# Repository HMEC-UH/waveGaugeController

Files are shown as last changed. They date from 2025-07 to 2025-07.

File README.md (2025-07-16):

# Introduction/General Project Overview

This project was created in conjunction with Dr. Troy Heitmann's Wave Energy Research lab. In their lab, they use "Wave Gauges" to take the required measurements for their work. However, the calibration and movement of these gauges is an important part of the setup and usage: often this process is manual, imprecise, and frustrating for Dr. Heitmann and his fellow researchers. The purpose of this project was to create an automated process for the calibration and movement of these "Wave Gauges." 

## Project Breakdown

This project can be broken down into the following segments:

1. Physical design of calibration setup
2. Fabrication of calibration setup
3. Design of electrical systems
4. Fabrication of electrical systems
5. TCP Socket Connection (Information Transfer)
6. Clear User Interface (GUI)

## Physical Design of Calibration Setup

The design for the physical movement of the wave gauge is relatively minimalistic and simple. Using an internally outputting cycloidal gearbox to actuate a T12x3mm pitch lead screw and a close loop Nema 23 (along with the CL57T-V4.1 stepper driver), this system has +-0.5mm of control over the vertical actuation of the gauge (which is attached via screw clamping mechanism). There is a parallel "backbone" in the form of 8020 1010 extrusion. The carrier and lower reciever for the lead screw use offset 8020 1010 extrusion profiles (0.15mm) to achieve proper tolerance when mounting, and use t-nuts to properly clamp and attach onto the 8020 back rail. 

## Design of Electrical Systems

Again, the design of the electrical systems for this project is relatively simple. Using an Arduino Uno WiFi REV2 wired to a CL57T-V4.1 stepper driver (all powered by a 24V variable power supply), this system is able to be controlled over local WiFi.

## Programming

The code for this project was aimed to allow for a python-based GUI (with active feedback) that could send desired movement over local WiFi. It was a challenge using the WiFiNINA Arduino library to properly parse incoming requests from the Python GUI, but using the available "requests" library and PyQt5 (for GUI design), developing these two components was not extremely complex.

# Using Posted Resources

## Posted Resources

This GitHub page has all of the .STEP files (editable geometry) for the entire system posted. Additionally, it has the python and accompanying Arduino code to implement and use the project.

## Notes on Code

Prior to usage, the user will have to import the following libraries on their computer (using a virtual environment and "pip" or "pipx"):

1. PyQt5
2. MatPlotLib
3. requests

All code for this project was develoed in Visual Studios Code, and should be fully understandable through the provided comments. 

Additionally, there is Arduino code posted for both Platform IO and the Arduino IDE. Just ensure that you are using the correct version. 

## Bill of Materials (BOM)

The bill of materials for this project are posted as a .csv file in the repository. 

# Assembly Overview

The assembly for this project is simple and straightforward, as is displayed throughout a few steps below.

## Cycloidal Assembly

### Step 1: Carrier Assembly

Assemble the carrier as displayed below. Use heat set inserts on the topside of the cycloidal output carrier.

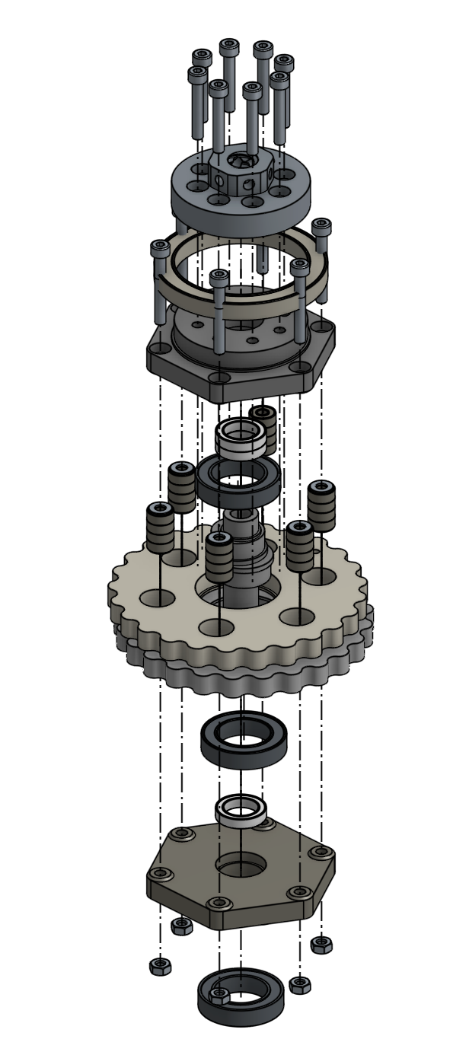
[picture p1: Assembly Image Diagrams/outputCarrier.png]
Carrier Assembly


### Step 2: Housing Assembly

Assemble the housing as shown below (insert the 50mmx6mm stainless steel dowels into the lower housing)

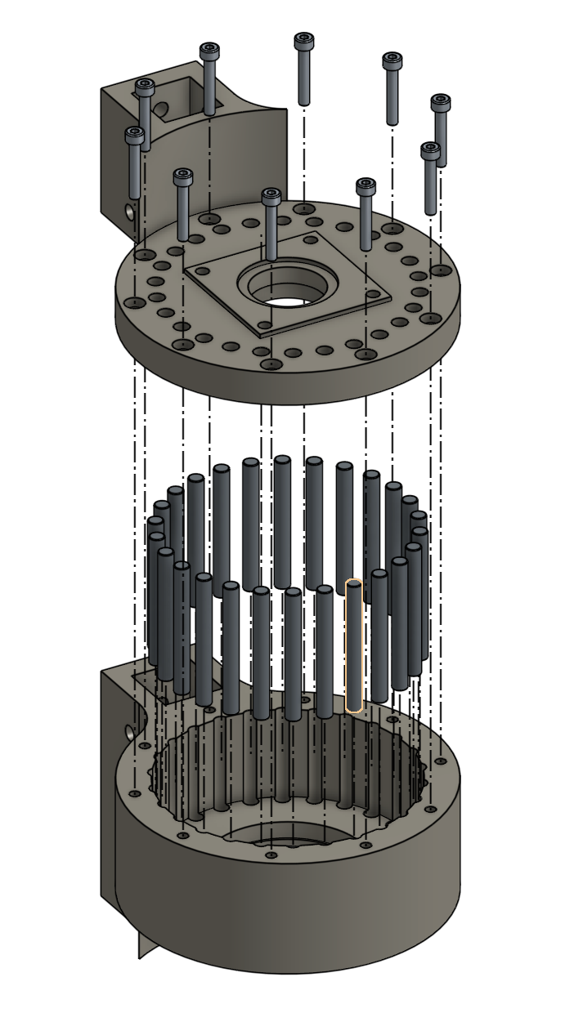
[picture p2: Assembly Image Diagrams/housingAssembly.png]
Housing Assembly


### Step 3: Motor Mounting

Screw the motor to the upper housing using M4x20mm bolts and M4 lock nuts.

### Step 4: Carrier Insertion and Upper Housing Mounting

Place the cycloidal disks into the housing as shown below, and screw on the upper housing (ensure that the D-Shaft bore of the eccentric bearing and the D-shaft of the motor are aligned. It should fit snugly). It will take some gentle pressure to ease the upper housing onto the gearbox. 

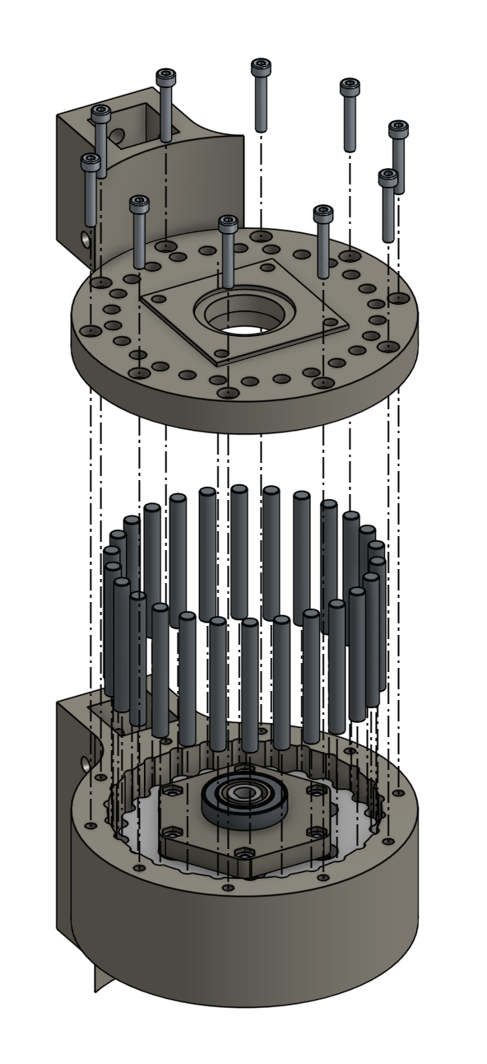
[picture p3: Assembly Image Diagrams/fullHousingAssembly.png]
Carrier Insertion


### Step 5: Output to Lead Screw

Screw the lead screw into the negative T12 thread on the output side of the cycloidal gearbox. 

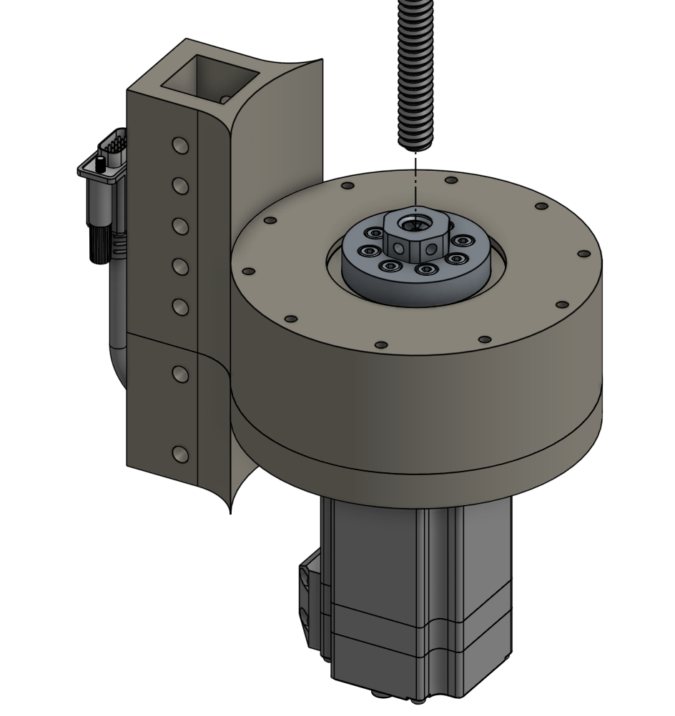
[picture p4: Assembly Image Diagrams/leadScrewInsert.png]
Lead Screw Insert


## Remaining Construction

### Step 1: Assemble Lower Receiver

Pressfit 32mmx20mmx7mm Bearing into the top and bottom parts of the lower receiver. Insert the lower negative lead screw thread in-between the two bearings, and then secure both parts together with screws. 

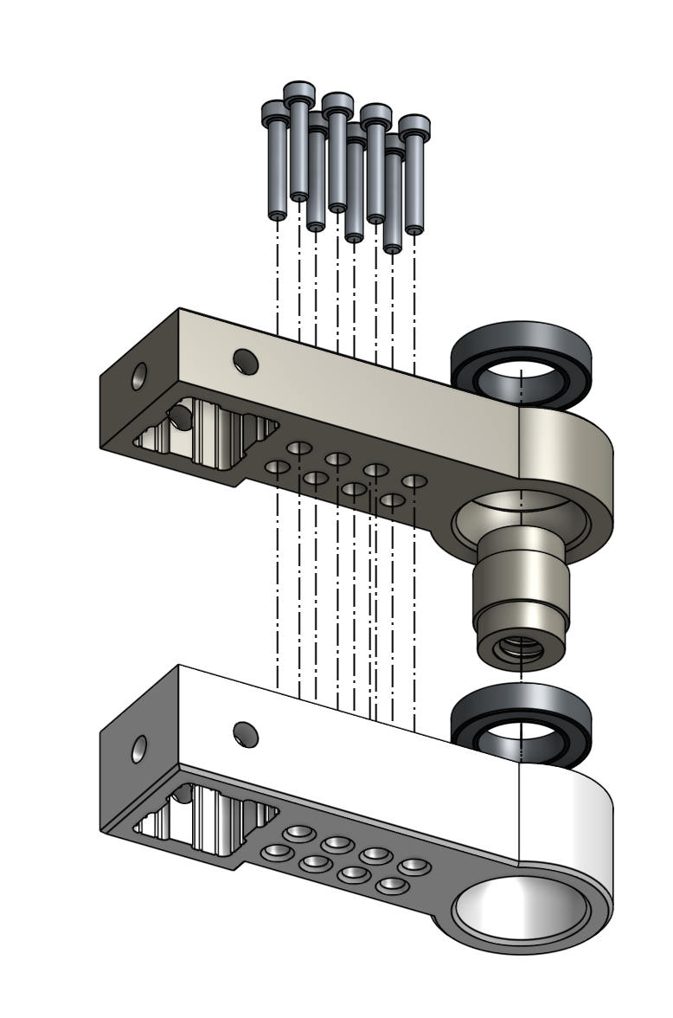
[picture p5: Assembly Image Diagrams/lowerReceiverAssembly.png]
Full Lower Assembly


### Step 2: Assemble Vertical Carrier

Attach the T12 Nut to the Vertical Carrier (using M4x30mm bolts and M4 locknut), and loosely screw in the clamp for the wave gauge. 

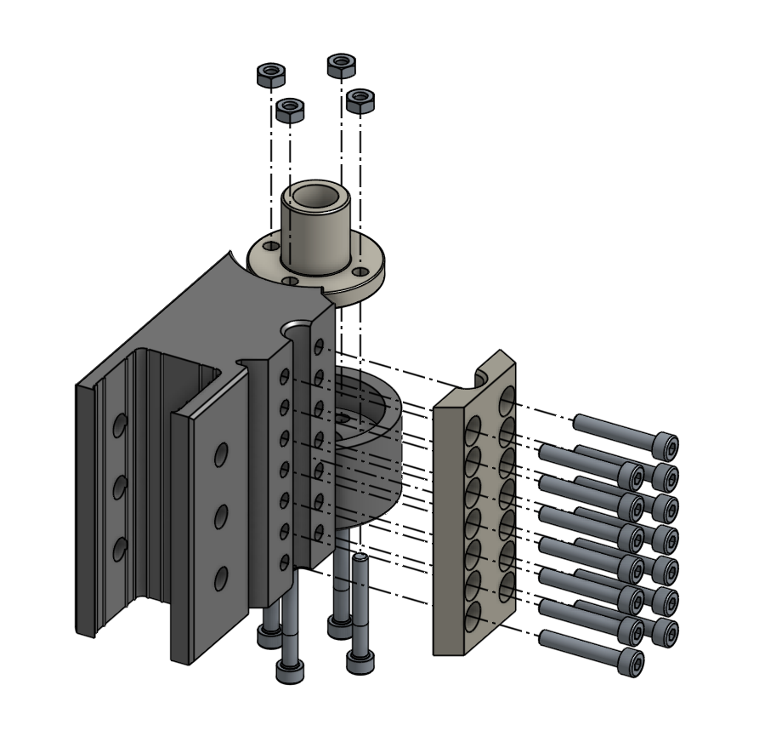
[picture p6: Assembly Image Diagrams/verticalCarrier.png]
Vertical Carrier Assembly


### Step 3: Full Assembly

Assemble the entire mechanism as displayed below. The stepper motor and gearbox should be mounted at the top of the lead screw/extrusion. The vertical carrier (with the copper nut) should be mounted somewhere approximately halfway down the lead screw (with the copper nut on the lead screw), with the negative offset 8020 1010 extrusion profile mounted over the extrusion. Finally, mount the lower receiver in the same fashion (the lower reciever negative thread should screw onto the lead screw). 

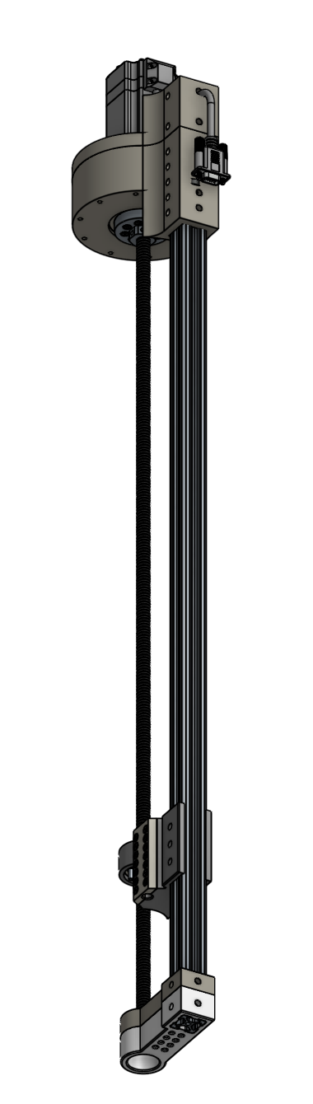
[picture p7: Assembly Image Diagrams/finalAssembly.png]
Final Assembly


# Developer Notes

I'm Charlie Koh. At the time of this development, I am a rising Junior at Punahou High School. This project was developed in collaboration with the lab of Dr. Troy Heitmann.

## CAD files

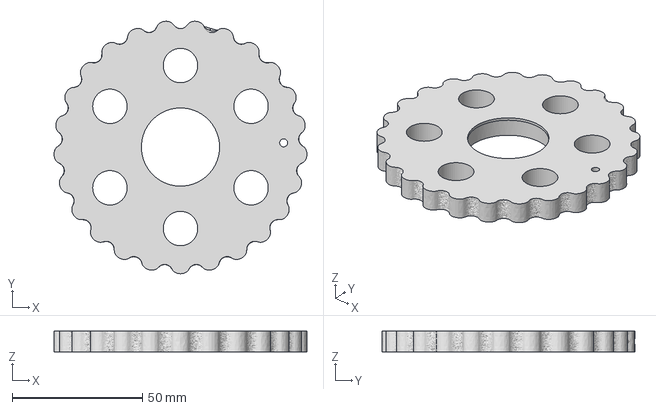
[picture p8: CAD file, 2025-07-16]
CAD Files/Cycloidal/Phased Cycloidal Disk (Tolerance -0.05mm).step
97.0 x 96.9 x 8.00 mm

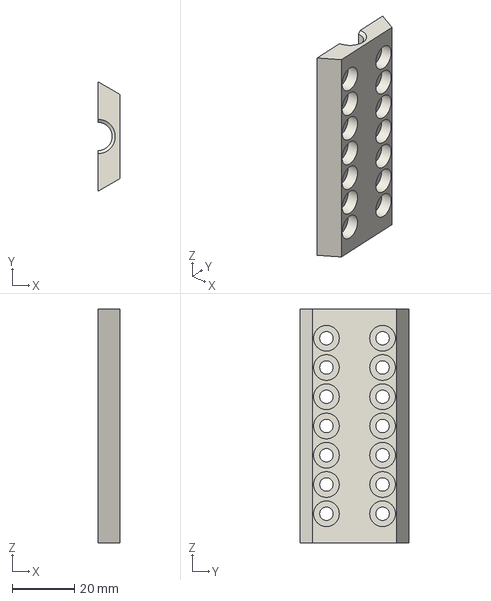
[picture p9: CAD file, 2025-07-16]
CAD Files/Misc/Vertical Carrier Clamp.step
7.00 x 35.1 x 75.0 mm

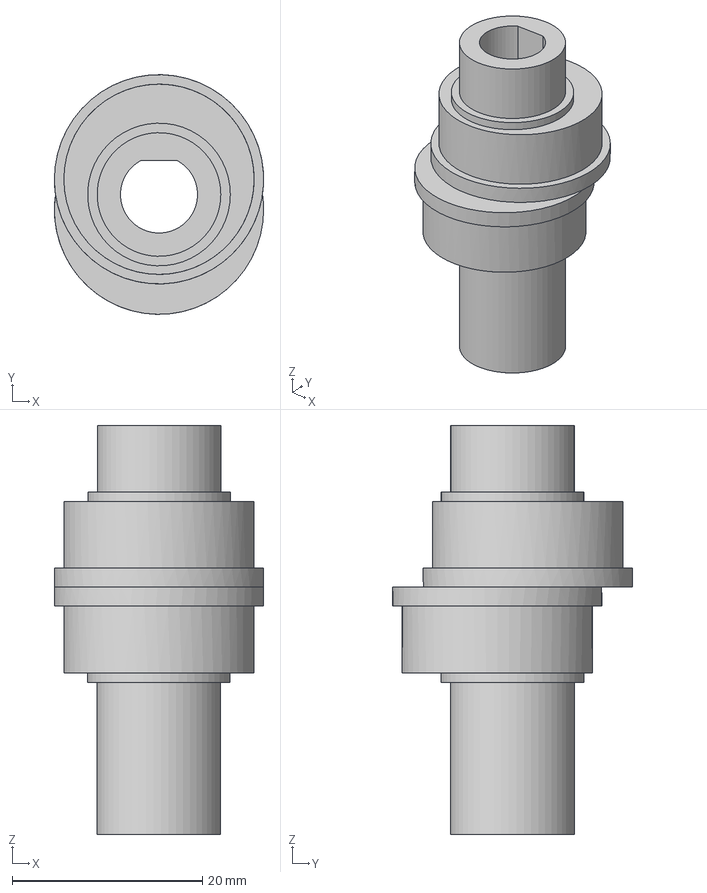
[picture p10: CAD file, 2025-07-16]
CAD Files/Cycloidal/Eccentric Bearing.step
22.0 x 25.2 x 43.0 mm

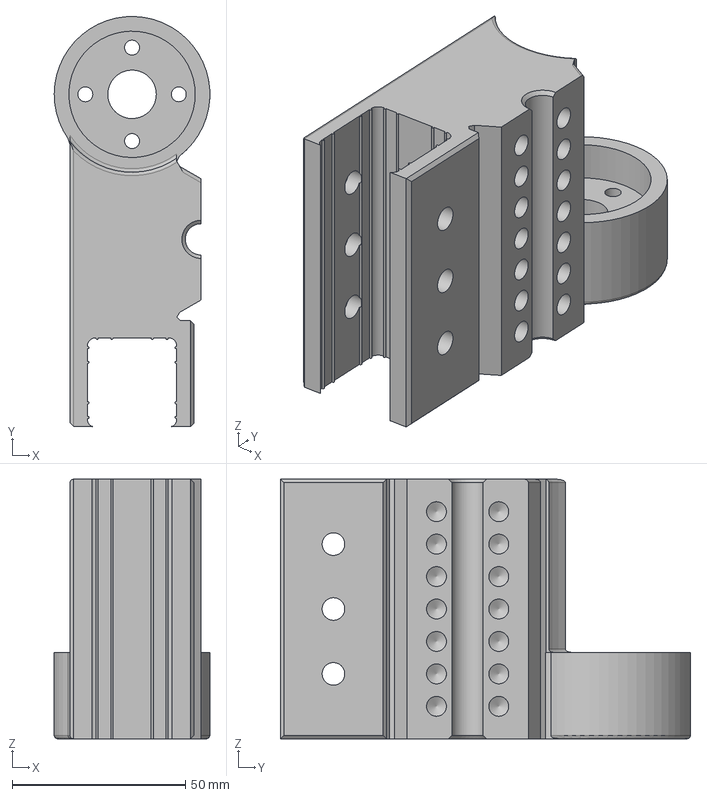
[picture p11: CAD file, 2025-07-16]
CAD Files/Misc/Vertical Carrier.step
45.0 x 118.5 x 75.0 mm

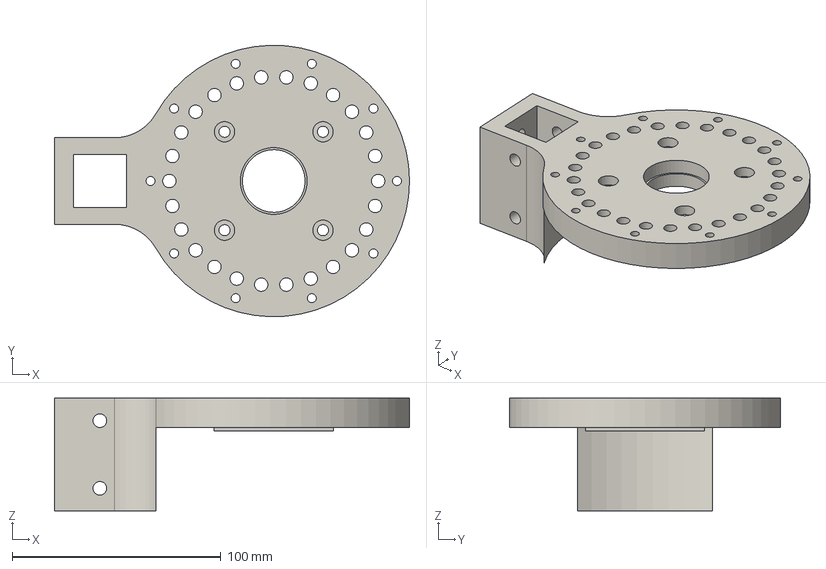
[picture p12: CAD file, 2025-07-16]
CAD Files/Cycloidal/Cycloidal Upper Housing.step
170.0 x 130.0 x 54.0 mm

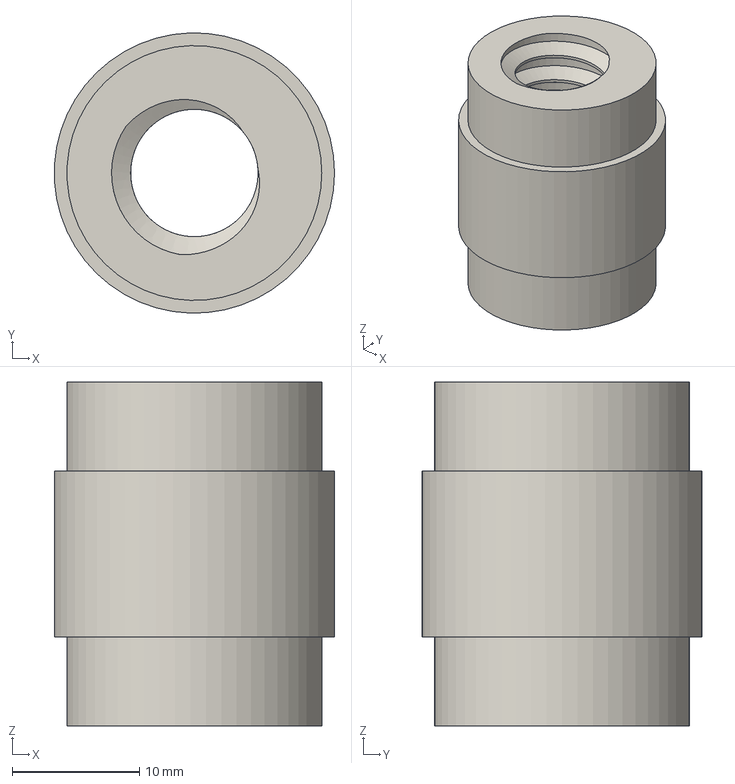
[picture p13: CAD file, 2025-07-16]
CAD Files/Misc/Lower Receiver Negative Thread.step
22.0 x 22.0 x 27.0 mm

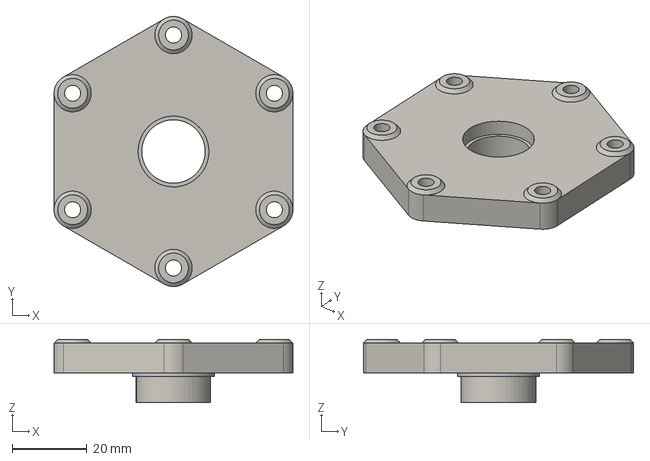
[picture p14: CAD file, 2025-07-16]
CAD Files/Cycloidal/Cycloidal Input Carrier.step
64.1 x 72.5 x 17.0 mm

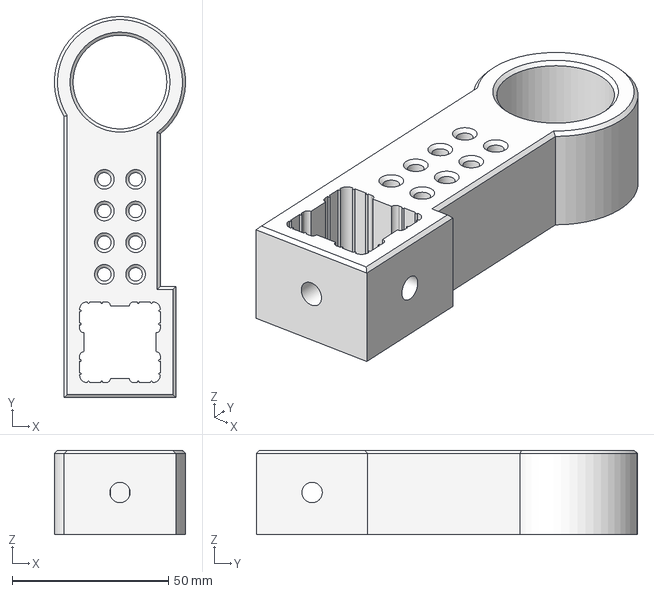
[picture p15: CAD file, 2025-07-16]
CAD Files/Misc/Lower Receiver Top.step
42.0 x 122.0 x 27.0 mm

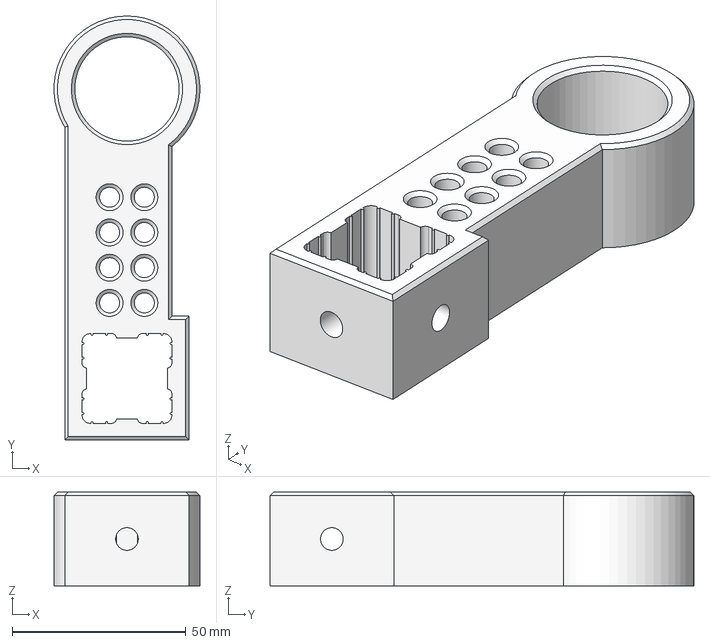
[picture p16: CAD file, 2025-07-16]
CAD Files/Misc/Lower Receiver Bottom.step
42.0 x 122.0 x 27.0 mm

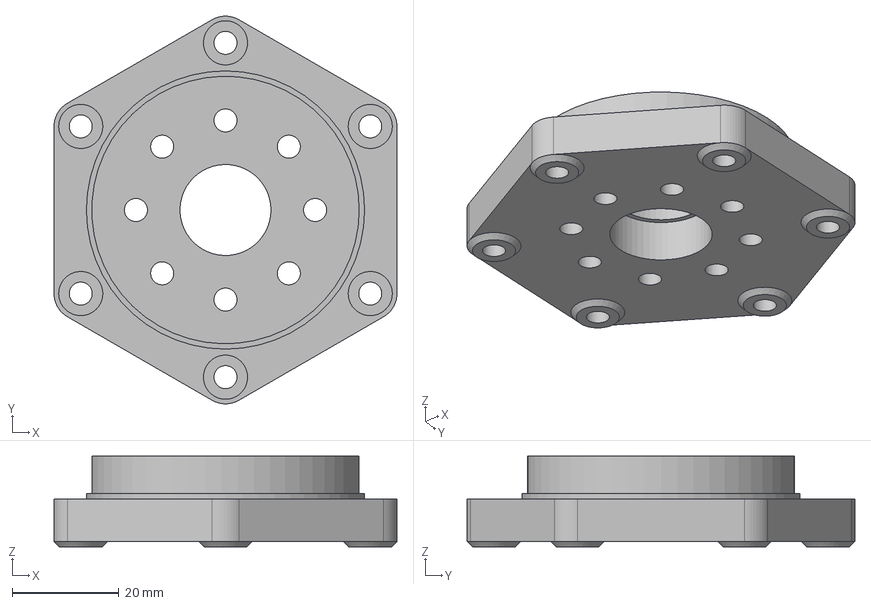
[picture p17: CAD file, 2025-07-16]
CAD Files/Cycloidal/Cycloidal Output Carrier.step
64.1 x 72.5 x 17.0 mm

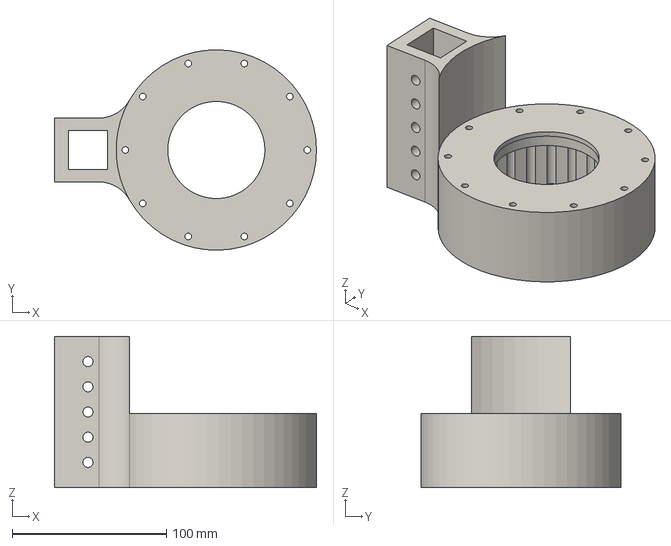
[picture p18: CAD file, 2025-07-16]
CAD Files/Cycloidal/Cycloidal Lower Housing.step
170.0 x 130.0 x 98.0 mm

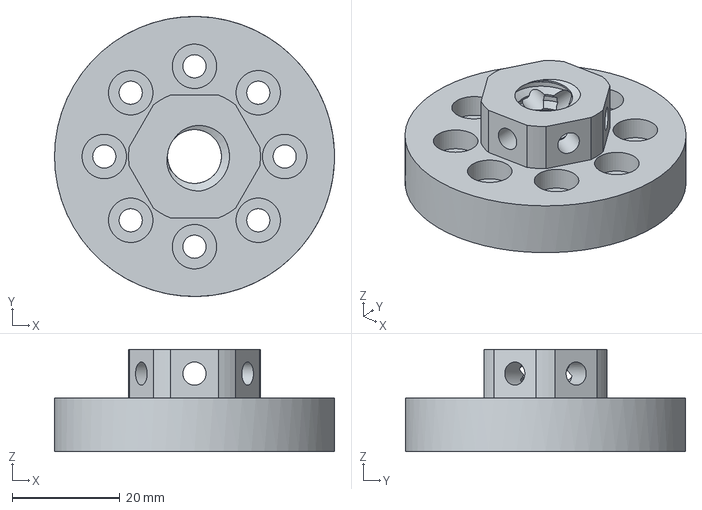
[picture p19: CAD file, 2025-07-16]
CAD Files/Cycloidal/Lead Screw Mounting Negative Thread.step
52.0 x 52.0 x 19.0 mm

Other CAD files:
CAD Files/Cycloidal/Cycloidal Disk (Tolerance -0.05mm).step

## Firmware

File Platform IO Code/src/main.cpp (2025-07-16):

// dependency: Arduino, WiFiNINA, AccelStepper
// This code is for an Arduino project that connects to WiFi, receives a value from a web request,
// and moves a stepper motor based on that value.
// It uses the AccelStepper library for controlling the stepper motor and WiFiNINA for WiFi connectivity.

#include <Arduino.h>
#include <Wire.h>
#include <SPI.h>
#include <WiFiNINA.h>
#include <AccelStepper.h>

char ssid[] = "HNEI (HIG 418)"; // your network SSID (name)
char pass[] = "WETSHne!1680"; // your network password

const uint8_t stepPin = 10; // Pin connected to the stepper motor step input
const uint8_t dirPin = 11; // Pin connected to the stepper motor direction input
const uint8_t enablePin = 13; // Pin connected to the stepper motor enable input

AccelStepper stepper(AccelStepper::DRIVER, stepPin, dirPin); // defining the stepper motor type and pins

WiFiServer server(80); // Create a WiFi server on port 80

int parseValue(String input) { // Function to parse the value from the input string
  int i = input.indexOf('value='); // Find the index of 'value=' in the input string
  if (i<0) {
    return -1; // If 'value=' is not found, return -1
  }
  String num = input.substring(i+1, i+6); // Extract the substring starting from 'value=' to the next 5 characters
  // Serial.print("Extracted number: ");
  // Serial.println(num);
  int space = num.indexOf(' '); // Find the index of the first space in the extracted number
  // Serial.print("Space found at: ");
  // Serial.println(space);
  if (space >= 0) { // If a space is found, trim the number to that point
    num = num.substring(0, space);
    Serial.print("Trimmed number: ");
    Serial.println(num);
  }
  return num.toInt(); // Convert the trimmed string to an integer and return it
}

void setup() { // Setup function to initialize the Arduino
  Serial.begin(115200); // Start serial communication at 115200 baud rate

  pinMode(enablePin, OUTPUT); // enabling the stepper motor
  digitalWrite(enablePin, LOW); 

  stepper.setMaxSpeed(10000); // Set the maximum speed of the stepper motor
  stepper.setAcceleration(2500); // Set the acceleration of the stepper motor

  while (WiFi.begin(ssid, pass) != WL_CONNECTED) {
    delay(1000);
  } // stays in this loop until the WiFi connection is established

  IPAddress ip = WiFi.localIP(); // returns the local IP address of the wifi module
  Serial.print("IP Address: "); // Print the local IP address to the serial monitor
  Serial.println(ip);

  server.begin(); // Start the WiFi server

  stepper.setCurrentPosition(0); // home the stepper motor position
}

void loop() { // Main loop to handle incoming requests
  WiFiClient client = server.available(); // Check if a client has connected to the server
  if (!client) {
    return; // If no client is connected cut the cycle short
  }

  String request = client.readStringUntil('\r'); // Read the incoming request from the client until a carriage return is found

  // Serial.println(request);
  
  int value = parseValue(request); // Parse the value from the request string

  // Serial.print("Parsed value: ");
  // Serial.println(value);
  
  // steps to move is calculated using the input value (in mm vertically moved)
  // The reduction attached to the stepper motor is 25:1, and the stepper motor has 200 steps per revolution.
  // The lead screw has a pitch of 3mm, so the number of steps to move is calculated as follows:
  // stepsToMove = (value in mm) * (reduction ratio) * (steps per revolution) / (pitch of lead screw)
  // In this case, the calculation is:
  // stepsToMove = (value in mm) * 25 * 200 / 3

  long stepsToMove = (long)value * (long)25 * (long)200 / (long)3;

  // Serial.println(stepsToMove);

  stepper.moveTo(stepsToMove);
  
  while (stepper.distanceToGo() != 0) {
    stepper.run();
  }

  // rezero after move is complete so that it can move the desired parse distance
  stepper.setCurrentPosition(0);
  
  client.println("HTTP/1.1 200 OK");
  client.println("Content-Type: text/plain");
  client.println("Connection: close");

  delay(1);
  client.stop();
}

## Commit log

2025-07-16 Full upload + README first draft
    [Cycloidal Disk (Tolerance -0.05mm).step, Cycloidal Input Carrier.step, Cycloidal Lower Housing.step, Cycloidal Output Carrier.step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]
2025-07-16 File Push + Assembly Update
